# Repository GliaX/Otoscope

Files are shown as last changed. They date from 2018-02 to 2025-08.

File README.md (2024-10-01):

Otoscope
========
This project aims to create a research-validated otoscope whose plans are
available freely and openly. The goal price is approximately USD$3 in parts. The current price is approximately USD$5.

Watch the trailer (https://youtu.be/aX0nkcNqGiI)

This design is based on current gold-standard designs of premium-brand
otoscopes.

The original design and work is by the talented Frankie Talarico. The license
is [TAPR OHL](https://github.com/GliaX/Otoscope/blob/master/LICENSE) where applicable.

* [Bill of Materials](docs/BILL_OF_MATERIALS.md)
* [Print guide](docs/PRINT_GUIDE.md)
* [Assembly instruction video](https://youtu.be/9h2voI1ipZM)
* [Lens assembly guide](docs/LENS_ASSEMBLY.md)
* [Otoscope assembly guide](docs/ASSEMBLY.md)

For an alternative speculum holder (like the one used by Spengler), please see this folder [here](https://github.com/GliaX/Otoscope/tree/master/speculum%20adapter).

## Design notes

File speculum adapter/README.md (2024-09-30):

printing informations: support required to ensure a good shape of the hole
the base shape has to be properly debured because it's a tight fit to ensure the stability of the adapter.

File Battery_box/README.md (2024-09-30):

printing informations: support required to ensure a good shape of the holes

It maintains the original size of the recommended one, ensuring a perfect fit in the "Battery holder".

To further improve cost-effectiveness and reduce dependency on online material ordering, there are two versions of electrical connections. One utilizes a self-made spring from any conducting metal wire, soldered to the wires. The other version uses parts purchased on Amazon for less than a dollar per set.

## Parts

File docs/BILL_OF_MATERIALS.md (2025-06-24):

Is a Link down? Tell us, and in the meantime while we fix it, google the listing title below to find the item/ alternatives. 

## AA battery case
#### Needs to be this exact model, due to the tight fitting nature on the holder in the 3D printed compartment
* [[Digikey](https://www.digikey.ca/product-detail/en/mpd-memory-protection-devices/BC12AAW/BC12AAW-ND/2439232) $1.90]

## 2.7 ohm resistor 
* [[Amazon](https://www.amazon.ca/dp/B0185FHBGC?ref=ppx_yo2ov_dt_b_fed_asin_title) $0.09]

## 5mm LED light
#### Really, any 5mm bright white LED could be used.  I like the one listed below because it is much brighter than any other LED light I've used.  Check the voltages of the LED you use, if the LED is rated for less that 3.2V, reassess which resistor you put into the circuit. 
* Amazon listing for the LED, listing titled "100pc 5MM White Round Water Clear Ultra Bright LED Light Diodes 30000 mcd - 40000 mcd (White)" [[Amazon CA](https://www.amazon.ca/100pc-White-Round-Bright-Diodes/dp/B0781Z96S6) $0.11 ($11.97/100pc)]

## Rocker Switch
#### Needs to be this model's dimension, due to the tight fitting nature of the switch in the 3D printed compartment
* Ebay listing for switch, listing titled "20x 250V 3A Mini Boat Rocker Switch SPST ON-OFF KCD1-2Pin Black Plastic Button" [[Ebay](https://www.ebay.com/itm/20x-250V-3A-Mini-Boat-Rocker-Switch-SPST-ON-OFF-KCD1-2Pin-Black-Plastic-Button-/141819484825) $0.25 ($5.00/ 20pc)]
* Ebay listing for switch, listing titled "10pcs Small Mini Black On/Off Boat Rocker Switch Rectangle10x15mm-SPST-2PIN V9A3" [[Ebay](https://www.ebay.ca/itm/10pcs-Small-Mini-Black-On-Off-Boat-Rocker-Switch-Rectangle10x15mm-SPST-2PIN-V9A3/264334026704?ssPageName=STRK%3AMEBIDX%3AIT&_trksid=p2057872.m2749.l2649) $0.15 ($1.55/ 10pc)]
* AliExpress Listing for switch, listing titled "10 pcs/lot KCD1 15 10mm 2PIN Boat Rocker Switch SPST Snap-in on off Micro switch Position 3A/250V Mini" [[Aliexpress](https://www.aliexpress.com/item/32880358926.html?spm=2114.search0302.3.1.5a7a118e4QEAbi&ws_ab_test=searchweb0_0,searchweb201602_0_10130_453_454_10618_536_317_537_319_10059_10696_10084_10083_10547_10546_10887_10307_321_10548_322_10065_10068_10103_10884_10545,searchweb201603_0,ppcSwitch_0&algo_pvid=8fdccf1d-54b3-4fad-b18d-6b211bd21dcf&algo_expid=8fdccf1d-54b3-4fad-b18d-6b211bd21dcf-0) $0.09 ($0.92/ 10pc)]

## 3x magnification lens
#### Below are two links to lenses that would work with the otoscope.  Following the [Lens Assembly Guide](https://github.com/GliaX/Otoscope/blob/master/docs/LENS_ASSEMBLY.md), you should manipulate the lens to fit in the holder. The Amazon listing below is the lens that fits the [new_lensjig2024.stl](https://github.com/GliaX/Otoscope/blob/master/lens_jig/new_lensjig2024.stl) part.  I recommend also checking local department stores for these items too. They can go by the name of "pocket reader", "3x magnifier with LED", and "Easy reader".  

* Ebay Listing for a pocket reader, listing titled "A Credit Card LED Magnifier Loupe with Light Case Magnifying Glass Utility [[Ebay](https://www.ebay.com/p/Credit-Card-LED-Magnifier-Loupe-With-Light-Leather-Case-Magnifying-Glass-Utility/3029465108?iid=362601347786&rt=nc) $2.39] 

* Amazon Listing for small 3x magnifying glasses, listing titled "Handheld Magnifier with Safety Lanyard (Set of 10)" [[Amazon CA](https://www.amazon.ca/gp/product/B008AK673Q/ref=ppx_yo_dt_b_asin_title_o01_s00?ie=UTF8&psc=1) $1.96 each]

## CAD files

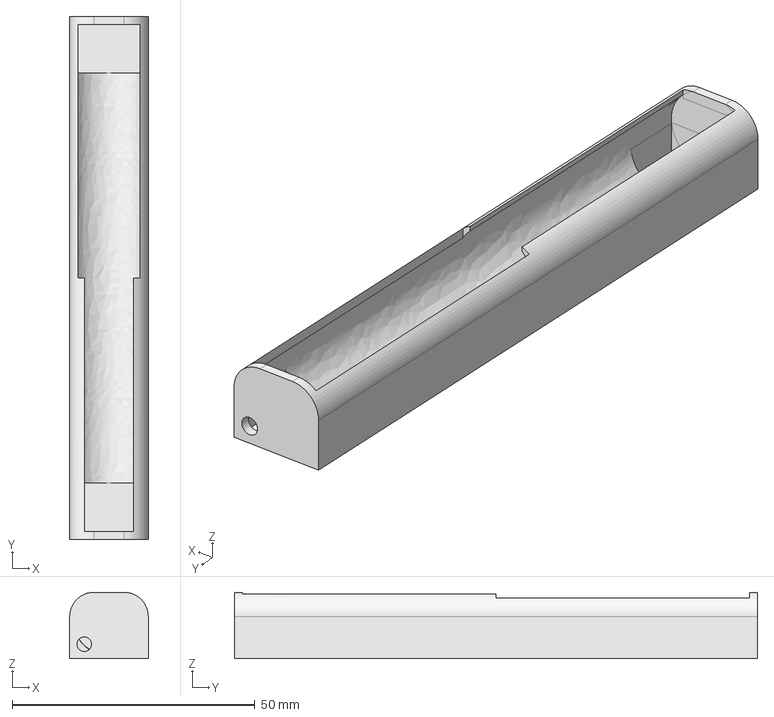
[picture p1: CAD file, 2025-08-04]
Battery_box/source file/Battery Box V3.fcstd
16.2 x 107.8 x 13.7 mm

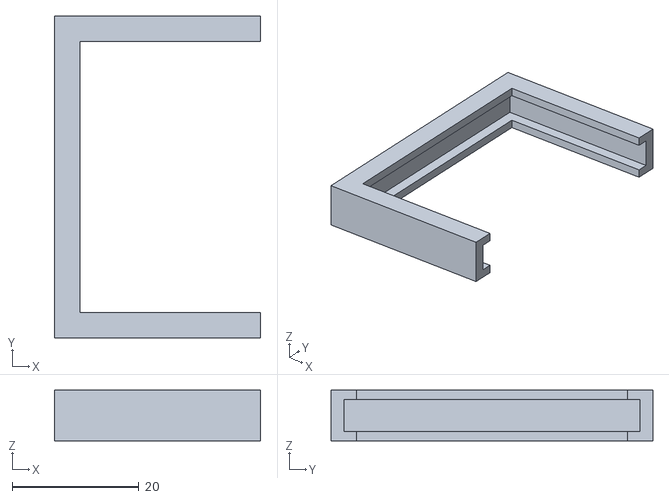
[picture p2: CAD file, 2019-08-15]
lens_jig/jig_1.stl
32.5 x 50.8 x 8.00

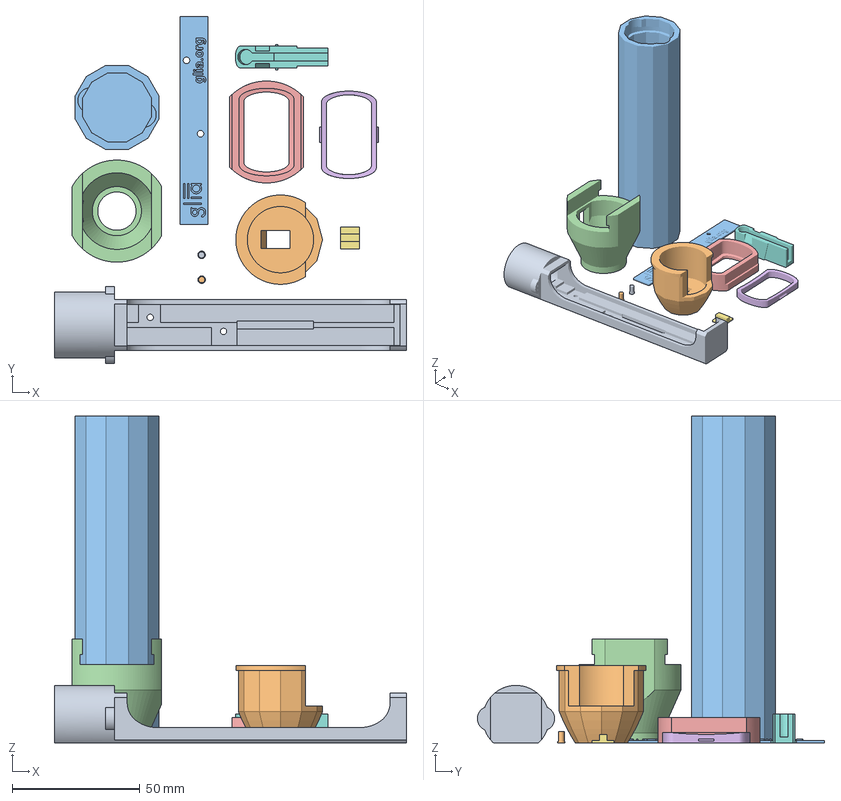
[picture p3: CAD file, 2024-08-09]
otoscope.3mf
137.9 x 136.1 x 128.0 mm
battery_holder.stl
button_cover.stl
handle.stl
head.stl
lens_large.stl
lens_small.stl
neck_cover_plate.stl
neck_led_holder.stl
plate_pin.stl
glia_name_plate (only logo and website).stl

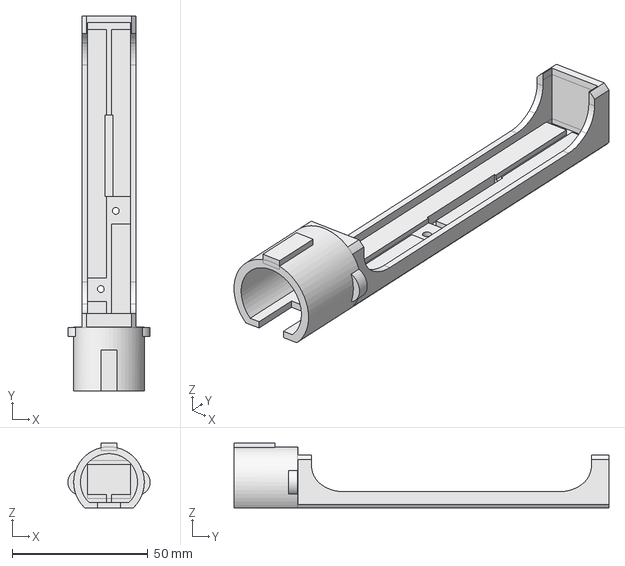
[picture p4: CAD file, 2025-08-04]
source_files/battery_holder2.FCStd
30.3 x 138.0 x 23.9 mm

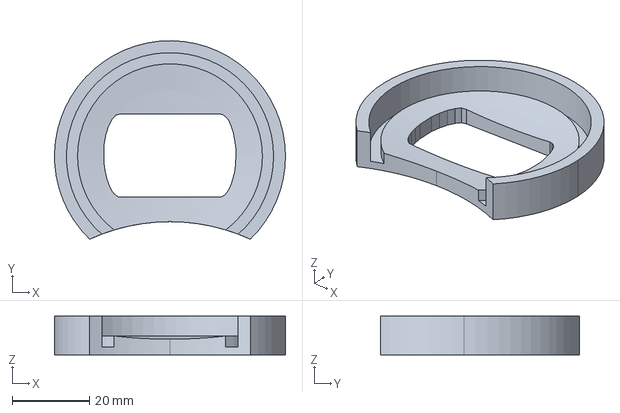
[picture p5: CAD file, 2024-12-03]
source_files/lens_jig/new_lensjig2024.FCStd
60.0 x 51.6 x 10.0 mm

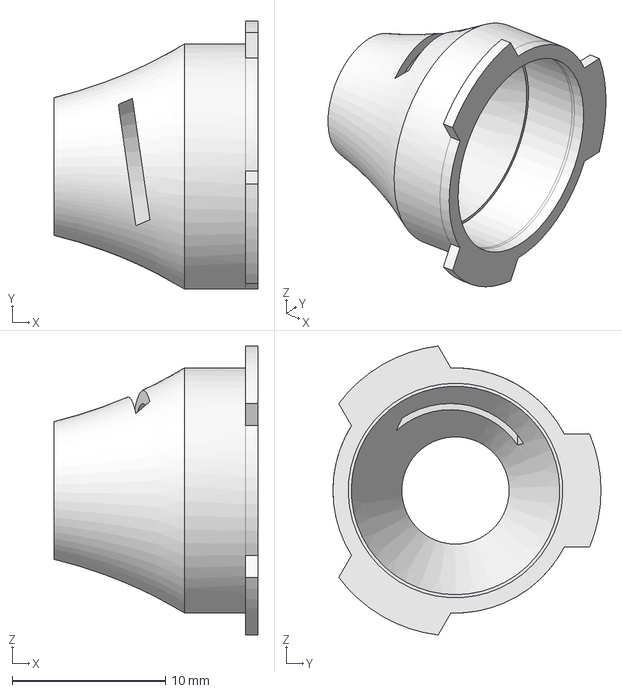
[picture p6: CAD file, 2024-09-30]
speculum adapter/source files/adaptater.FCStd
13.3 x 17.5 x 18.9 mm

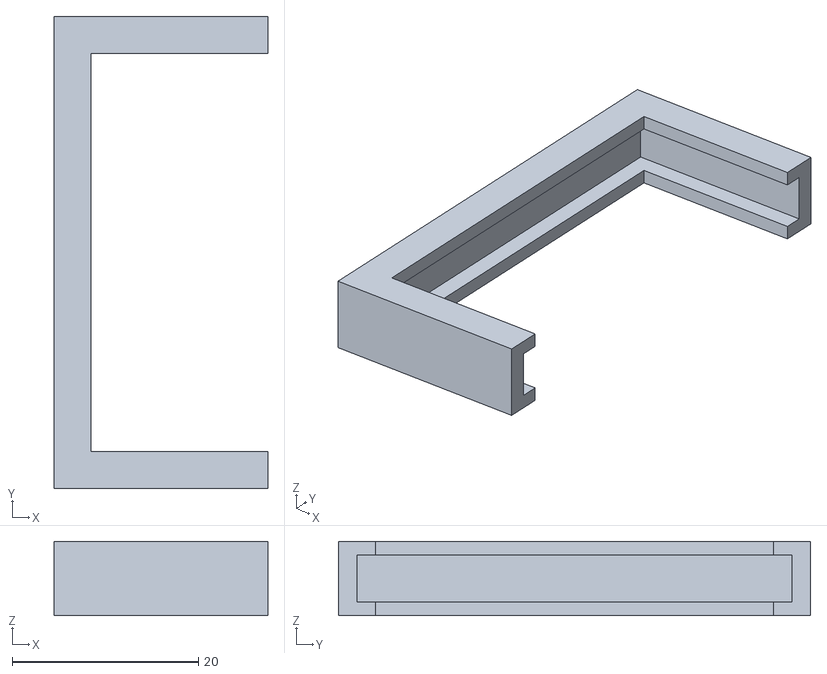
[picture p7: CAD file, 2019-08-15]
lens_jig/jig_2.stl
23.0 x 50.8 x 8.00

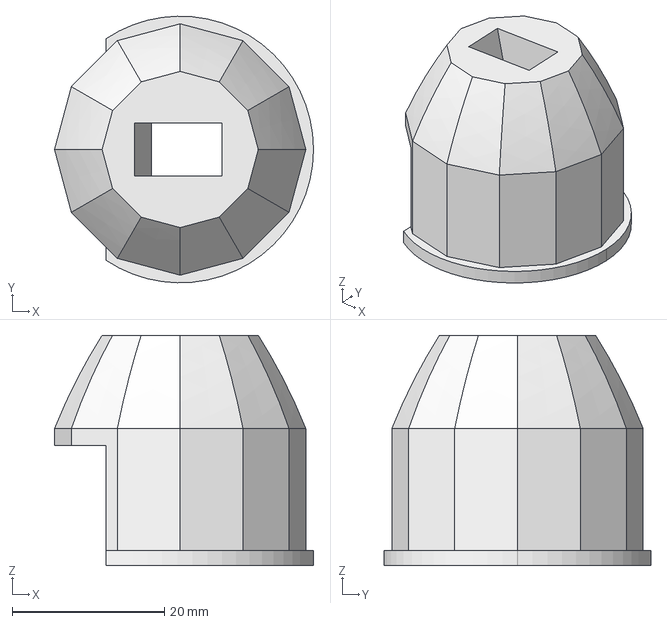
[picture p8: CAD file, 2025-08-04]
source_files/button_cover2.FCStd
34.0 x 35.0 x 30.3 mm

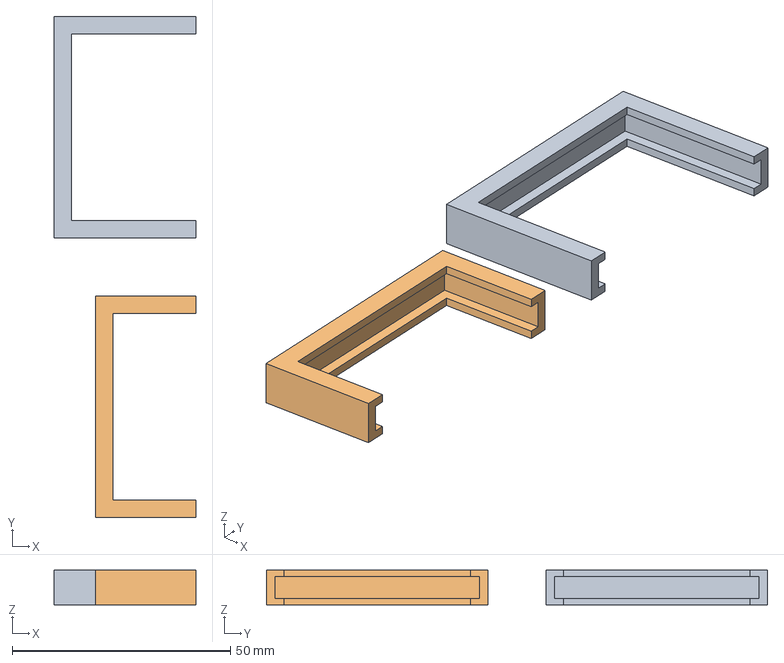
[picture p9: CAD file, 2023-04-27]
source_files/lens_jig/lens_jig.FCStd
32.5 x 114.8 x 8.00 mm
jig_1_src
jig_2_src

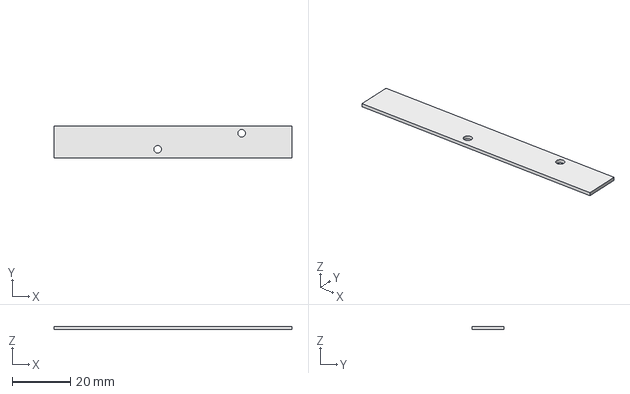
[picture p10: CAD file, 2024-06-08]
source_files/label_plate.FCStd
81.5 x 11.0 x 1.00 mm

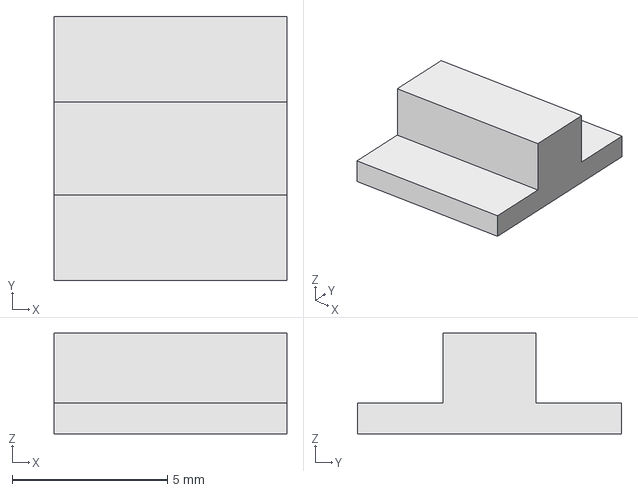
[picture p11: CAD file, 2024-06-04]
source_files/neck_cover_plate.FCStd
7.50 x 8.50 x 3.25 mm

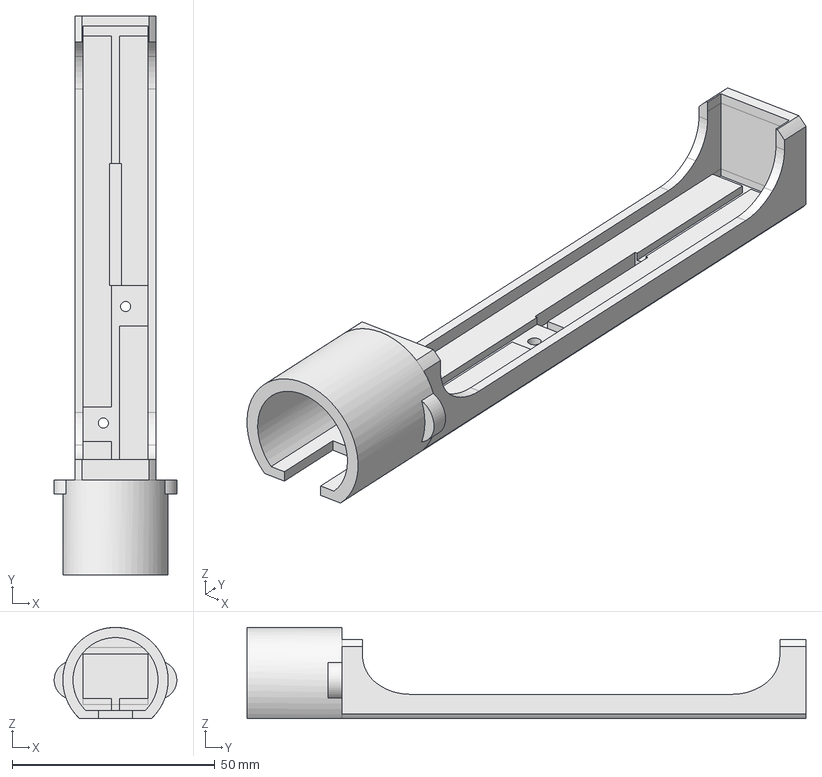
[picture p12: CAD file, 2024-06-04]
source_files/battery_holder.FCStd
30.3 x 137.9 x 22.5 mm

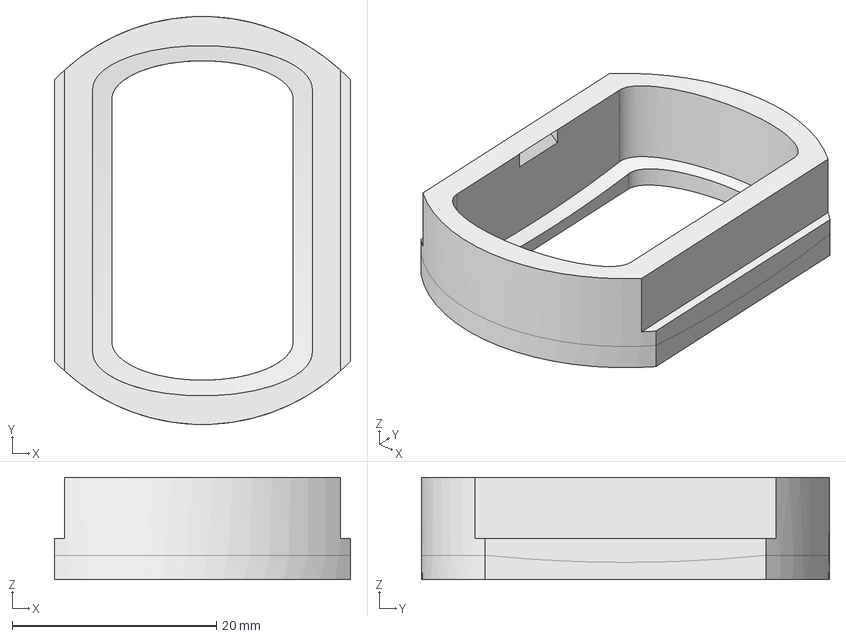
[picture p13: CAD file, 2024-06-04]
source_files/lens_large.FCStd
29.0 x 40.0 x 10.0 mm

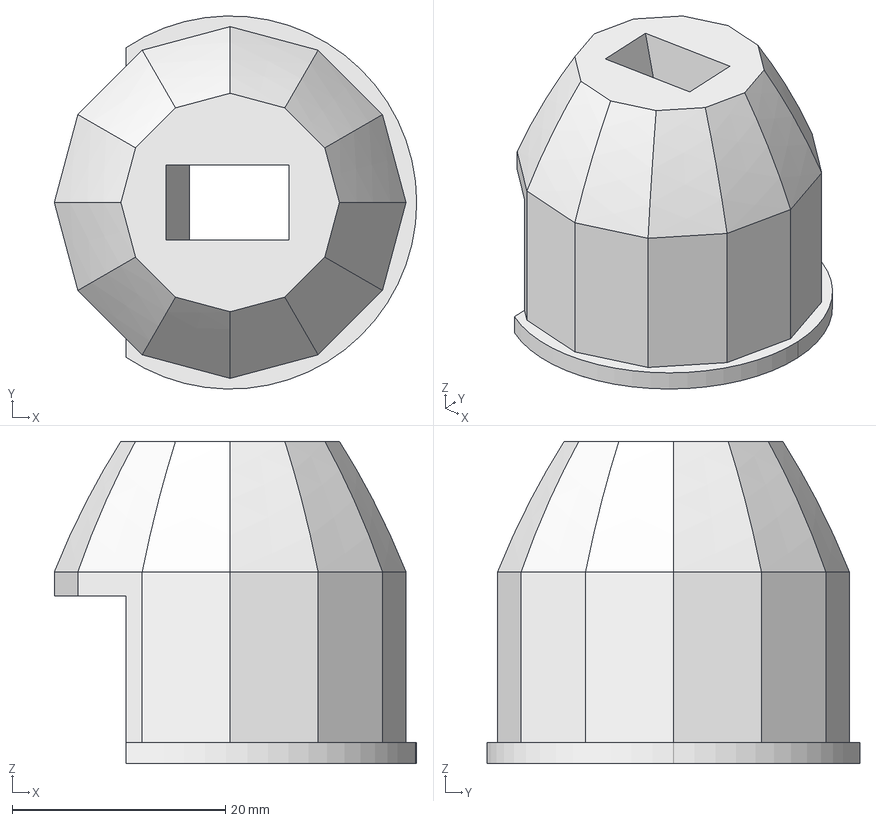
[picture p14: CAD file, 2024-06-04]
source_files/button_cover.FCStd
34.0 x 35.0 x 30.3 mm

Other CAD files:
Battery_box/source file/BatteryBoxV3-Corps.stl
source_files/neck_led_holder.FCStd
source_files/plate_pin.FCStd
source_files/head.FCStd
battery_holder.stl
button_cover.stl
handle.stl
head.stl
label_plate.stl
lens_jig/new_lensjig2024.stl
lens_large.stl
lens_small.stl
neck_cover_plate.stl
neck_led_holder.stl
plate_pin.stl
source_files/handle.FCStd
source_files/lens_jig/jig_1.obj
source_files/lens_jig/jig_2.obj
source_files/lens_small.FCStd
source_files/specula.FCStd
specula.stl
speculum adapter/source files/adaptater.stl

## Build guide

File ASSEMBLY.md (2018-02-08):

# Otoscope Assembly Guide

This document outlines the manufacture of a high-quality low-cost open source otoscope. In this document, we will assemble main otoscope body, including the otoscope head, neck and battery area. Lens creation is [covered in a separate guide](LENS_ASSEMBLY.md).

You will need the following:

* Printed parts:
  * Battery holder
  * Button holder
  * Handle cover
  * Inner head
  * LED chamber
  * Outer head

* Other parts:
  * Completed [lens assembly](LENS_ASSEMBLY.md)
  * Battery compartment x 2 ([amazon]())
  * Momentary switch ([amazon]())
  * 
  * Cyanoacrylate glue ([amazon](https://www.amazon.ca/Gorilla-7805201-20g-Super-Glue))
  * Clamps ([amazon](https://www.amazon.ca/TEKTON-3901-4-Inch-Opening-10-Piece))

## Step 1
Prepare printed parts and acquire other parts as necessary. Below are all required printed parts except for the handle cover and the bottom half of the LED chamber. All pieces should be printed in black, but the LED chamber top can be printed in white for extra LED light reflectance. 

Parts for otoscope assembly

## Step 2
Sand the bottom of the neck piece and the square holder area of the battery holder. Sand or file the connector appendage until a tight fit is achieved.

Battery and neck pieces

## Step 3
Glue the neck piece and the battery compartment

Assembled battery and neck pieces

## Step 4
Prepare battery compartment. Roughly sand bottom of battery compartment for better glue exposure. 

Battery compartments with wiring
Battery compartments with soldering between

## Step 5
Place wiring through the slot in the battery holder. Glue the battery compartments to the battery holder.

Battery compartments with wiring through battery holder
Battery compartments glued to battery holder

## Step 6
Prepare button.
	
Feed button wires through the button holder.  Placed button in the button holder and super glue.

Solder one button wire to the positive wire from battery holders. 

Create the LED chamber.

I placed a 220 ohm pull-up resistor here, I took this out after the fact because the lights were too dim. 

Super glue LED chamber bottom half. 
Super glue LED chamber to the otoscope inner head. 

Feed wires through otoscope neck conduit.  Place otoscope inner head inside the otoscope outer head. 

Super glue the inner head piece on the outer head piece. 

Connect otoscope head to battery part. 

Slide excess wire into neck section of otoscope. 
Super glue the two parts.

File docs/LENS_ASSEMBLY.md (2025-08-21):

# **Lens Assembly Guide**

*This document explains how to make the lens for the current version of the Glia Otoscope.*

You will need the following:
         
        3D Printed Parts:
        ◦ Lens holder (large)
        ◦ Lens holder (small)
        ◦ Lens jig  (new_lensjig2024.stl)
        
        Other:
        ◦ Lens, 3x magnification 
        ◦ Masking tape
        ◦ Pen or fine marker
        ◦ Saw
        ◦ Sander

**Step 1**

Cover back and front of lens with masking tape to protect it.

lens with tape on it

**Step 2**

Place lens jig over lens. Use pen or fine marker to trace shape onto lens, as close to lens jig as possible. Then take lens jig off of lens.

jig on lens trace outline

pen outline

**Step 3**

Carefully use a saw to roughly cut out the traced shap, keeping just outside of traced line. 

cut out lens

**Step 4**

Carefully use sander to refine cut out lens so that it will fit snugly into large lens holder. It is recommended to go slow, and try the fit after each time you sand to make sure you get a snug fit and don’t sand the lens too small. Sand the lens to get as close to the traced line as possible.

There should not be any gaps between the lens and the large lens holder.

lens in lens holder

**Step 5**

Once the lens fits snugly into the large lens holder, carefully take off the masking tape without touching the face of the lens, and push it all the way into the large lens holder. Then push the small lens holder in to secure the lens in the holder.

The fit should be snug enough that you do not need to secure the lens in the holder with glue.

tape off lens small lens holder holding in lens

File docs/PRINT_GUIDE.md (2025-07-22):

# Print Guide

This document explains how to orient and print the various printed parts. This guide uses [Slic3r](http://slic3r.org/)

## Print settings

All parts (other than the handle) should be printed with an infill of 100% and layer height of 0.2mm.  

*The handle should be printed with an infil of 20%.*

A couple of tips when printing in Petg:
<br>
If you have trouble getting the battery_holder and handle to fit properly, print the handle at 2% larger, and the battery_holder at 1% smaller (the wired battery case should still fit when the bottom edges are trimmed). If you have trouble getting the neck_led_holder to fit the button cover, print it at 2% smaller (and then print the neck_cover_plate at 2% smaller as well so that it will fit the led holder).

## Supports

The following parts can be printed without any supports from the 3mf file uploaded:
  * Handle
  * Label plate
  * Lens large
  * Lens small
  * Neck cover plate
  * Neck led holder
  * Plate pins
  * Button cover
  
The following should be printed with supports:
  * Battery holder (full supports)
  * Head (supports on build plate only)

## Orientation
Orient the parts as in the build plate below:
Slic3r bed with all parts

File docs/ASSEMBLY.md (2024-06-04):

# Otoscope Assembly Guide

This document outlines the manufacture of a high-quality low-cost open source otoscope. In this document, we will assemble main otoscope body, including the otoscope head, neck and battery area.

You will need the following:

* Printed parts (See [Print guide](/docs/PRINT_GUIDE.md)):
  * Handle
  * Battery Holder
  * Head
  * Button Holder
  * Label Plate
  * Lens Large
  * Lens Small
  * Neck Cover Plate
  * Neck LED Holder
  * Plate Pins

* Other parts:
  * 3x acrylic lens
  * AA Battery holder 
  * Switch 
  * 5mm LED light 
  * Cyanoacrylate glue 
  * Soldering iron
  * Solder
  * Small gauge wire
  * Electrical tape or shrinkwrap wire cover

Watch the youtube video tutorial here on how to build the otoscope:
https://youtu.be/9h2voI1ipZM

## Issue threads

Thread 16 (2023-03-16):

### ISSUE TITLE
Suggested simplified versions of 2 CAD files from forum

### ISSUE THREAD

**Issue by tareko** [GliaX/Otoscope#16]
Hello @0penBrain and @mwganson.

User `kisolre` on the FreeCAD forums submitted "[a simplified sketch of the specula_holder](https://forum.freecadweb.org/viewtopic.php?f=8&t=38643&p=330601#p330584)" and a "[head lock recreated in PartDesign with proper ellipses](https://forum.freecadweb.org/viewtopic.php?f=8&t=38643&p=330601#p330597)".

Could you guys comment on whether these files supersede yours or what I should do about this?

Thank you

tarek : )

**Comment by mef51** [comment]
I've modified kisolre's `head_lock` model with parabolas instead of ellipses and added a longer tail as part of the assembly changes in PR #19.

I've also updated the main branch with kisolre's simpler sketch in `specula_holder` and simplified the pocket features

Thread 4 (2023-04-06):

### ISSUE TITLE
Why are there no CAD files?

### ISSUE THREAD

**Issue by luzpaz** [GliaX/Otoscope#4]
I'm part of the FreeCAD community outreach team. There are a lot of volunteers on the forum that could be willing to help in this very cool endeavor. Feel free to post on our [Forums](https://forum.freecadweb.org/) to showcase your work or ask for help. 

Examples:  
* [3D printed canine hind limb](https://forum.freecadweb.org/viewtopic.php?t=26901)
* [Anyone interested in donating their time to make a clubfoot brace?](https://forum.freecadweb.org/viewtopic.php?t=27168)  
* [Open Source Ecology](https://wiki.opensourceecology.org/wiki/FreeCAD_101) onboards their community with FreeCAD  
etc...

**Comment by tareko** [comment]
Thank you so much @luzpaz ! I'll look and post in the next day or two.
Our experience is such a testament to the need for FreeCAD, and why we base our work on FreeCAD and OpenSCAD as well. Thank you!

**Comment by eddriesen** [comment]
I'm creating the files as we speak. Please do mind that freecad is new to me. So bare with me. 
 
Things i'm figuring out atm.;
- part / body / project structure
- ok to use assembly2 module (prime time?/ Getting an error on 0.18.3)
- seperate proj file for each component vs project file with multiple parts or bodies vs seperate files and assembly2 project file
- any topdown / associativity possible?

**Comment by luzpaz** [comment]
No, Assembly2 is deprecated. Better to use Assembly2+ or Assembly3.  
Please open a thread on the FreeCAD forums to discuss with the community. Thanks!

**Comment by tareko** [comment]
Thanks for the advice @luzpaz . Will open the thread tonight and post here.

**Comment by tareko** [comment]
[Posted to the FreeCAD forums](https://forum.freecadweb.org/viewtopic.php?f=31&t=38643)

**Comment by rewolff** [comment]
I read you wanted help in converting to openscad (or freecad which I don't know). 
I have started a bit, but it is much more difficult than expected. For example, The "button_block" looks as if it is the difference between three rectangular blocks (with critical parameters 18.45, 1.398, 12.747 and 13.000) and a sphere. But it turns out that sphere is not a sphere. So.... To help me: What kinds of shapes are involved in an object like the button_block ???

**Comment by tareko** [comment]
Hi @rewolff! Just a quick note that there seems to be an active effort to do this in FreeCAD at the moment, which I think is more fit for purpose. You are welcome to continue in OpenSCAD, but you may feel this work is duplicating the work of others.

Regarding your specific query, I have poked @Frankie-E4Rdesigns about this to answer you more specifically. I don't think your replica is obliged to be 1:1, though obviously the pieces will have to fit together in the end.

Thank you again!

tarek : )

**Comment by Frankie-E4Rdesigns** [comment]
Specula Holder, Handle cover, button lock, neck part, button block, and handle coupler all look great!

**Comment by tareko** [comment]
OK, I figure instead I'm going to get rid of the PRs above and keep a list of TODO parts. This is a duplicate of the FreeCAD thread's list.. I'll keep it on the [first post I made](https://github.com/GliaX/Otoscope/issues/4#issuecomment-521977767).

**Comment by 0penBrain** [comment]
@tareko : regarding both lens holders, as it can be some critical parts, I think it is necessary that we can get a 3D model or mechanical drawing of the lens itself (or eventually some optical/mathematical description of it). May you provide that ?

**Comment by Frankie-E4Rdesigns** [comment]
Good idea on the lens schematics, will post something on that soon. 
Different 3x magnification lenses will have slightly different dimensions, but I will post about the one I use.

**Comment by mef51** [comment]
PR #19 adds freecad files for
* inner_head
* outer_head
* lens_holder_bottom

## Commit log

2015-04-01 initial commit of phone-mounted otoscope setup
    [phonemountotoscope.scad, phonemountotoscope.stl]
2018-01-25 Replace old files with new standalone model
    [battery_holder.stl, button_holder.stl, inner_head.stl, led_chamber.stl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]
2018-01-25 Add handle cover
    [handle_cover.stl]
2018-02-07 Add OBJ source files for STLs
    Exported directly from TinkerCAD with the materials removed
    [battery_holder.obj, button_holder.obj, handle_cover.obj, inner_head.obj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]
2018-02-07 Add lens jig STL and source files
    [jig_1.obj, jig_1.stl, jig_2.obj, jig_2.stl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]
2018-02-07 First iteration of Assembly document as written by @Frankie-E4Rdesigns
2018-02-07 Add lens assembly instructions
2018-02-07 First version of Assembly instructions as written by @Frankie_E4RDesigns
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2018-02-09 Repaired STL
    [inner_head.stl]
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2019-08-14 Upgrade to version 3.0 files
    [battery_holder.obj, battery_holder.stl, button_block.obj, button_block.stl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]
2019-08-15 Update to new jig files
    [jig_1.obj, jig_1.stl, jig_2.obj, jig_2.stl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]
2019-08-15 Add Otoscope plate as 3MF
    [otoscope.3mf]
2019-08-26 head_lock, name_plate, name_plate_locks
    [head_lock.FCStd, name_plate.FCStd, name_plate_locks.FCStd]
2019-08-27 tilt head_lock 3 degrees
    [head_lock.FCStd]
2019-08-27 tile head_lock 3 degrees
    [head_lock.FCStd]
2019-08-27 Move all files to regular source and adapt name_plate to relative paths
    [head_lock.FCStd, name_plate.FCStd, name_plate_locks.FCStd]
2019-08-28 specula_holder initial release => check geometry OK
    [specula_holder.FCStd]
2019-08-28 handle cover => Check geometry OK // Splines approximated with arcs
    [handle_cover.FCStd]
2019-08-28 button lock initial release => Check geometry OK
    [button_lock.FCStd]
2019-08-28 neck part initial release => Check geometry OK
    [neck.FCStd]
2019-08-28 button block initial release => Check geometry OK
    [button_block.FCStd]
2019-08-29 remove a useless remaining object used for modeling
    [button_lock.FCStd]
2019-08-29 button holder initial release
    [button_holder.FCStd]
2019-08-30 Move to proper source folder
    [specula_holder.FCStd]
2019-08-30 Move to correct source_files folder
    [handle_cover.FCStd]
2019-08-30 Move files to correct source folder
    [button_block.FCStd, button_lock.FCStd, neck.FCStd]
2019-08-30 button holder bottom initial release
    [button_holder_bottom.FCStd]
2019-08-30 Add lens jig from Kisolre
    [lens_jig.FCStd]
2022-12-06 add glia name plate
    [glia_name_plate.FCStd, glia_name_plate.stl]
2023-01-16 import outer_head into freecad and make one lock larger for easier assembly
    [outer_head_largerlock.3mf, outer_head_largerlock.FCStd, outer_head_largerlock.stl]
2023-01-18 add clearance on inner head edge, extend head lock tail, larger head hole
    [head_lock.FCStd, head_lock.stl, inner_head.stl, outer_head_import.FCStd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]
2023-01-18 add clearance to inner head edges and flatten bottom of outer head lock hole
    [inner_head.stl, outer_head_import.FCStd, outer_head_largerlock.stl]
2023-01-24 add backing to bulb feed on inner head for better printing.
    fix broken stl of outer head
    [inner_head.stl, outer_head_import.FCStd, outer_head_largerlock.stl]
2023-02-01 add remodel of inner head
    [inner_head.FCStd]
2023-02-02 fix topo naming problem on inner head
    [inner_head.FCStd]
2023-02-07 add model of lens_holder_bottom.
    Freecad boolean doesn't seem to work so no spherical contour for the lens
    [lens_holder_bottom.FCStd]
2023-02-07 add lens_holder_bottom thanks to Shalmeneser on freecad forums
    https://forum.freecad.org/viewtopic.php?p=659133#p659133
    [lens_holder_bottom.FCStd, lens_holder_bottom.stl]
2023-02-08 add remodel of outer head
    [outer_head.FCStd, outer_head.stl, outer_head_largerlock.stl]
2023-02-14 adjust outer and inner heads for assembly
    [inner_head.FCStd, inner_head.stl, lens_holder_bottom.FCStd, outer_head.stl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]
2023-02-15 add lens_holder_top, remove imported freecad meshes,
    [lens_holder_top.FCStd, lens_holder_top.stl, outer_head_import.FCStd]
2023-02-20 remodel battery holder in freecad
    [battery_holder.FCStd, battery_holder.stl]
2023-03-16 move button_holder and add stl from freecad file
    [button_holder.FCStd, button_holder.stl]
2023-03-16 move button_holder_bottom and add stl
    [button_holder_bottom.FCStd, button_holder_bottom.stl]
2023-03-16 add freecad model of handle_coupler
    [handle_coupler.FCStd, handle_coupler.stl]
2023-03-16 import kisolre's head_lock, replace ellipses with parabolas, extend tail
    original file from
    https://forum.freecad.org/viewtopic.php?f=8&t=38643&p=330601#p330597
    part of issue #16
    [head_lock.FCStd, head_lock.stl]
2023-03-16 update specula_holder model with kisolre's sketch, simplify pockets
    kisolre's sketch:
    https://forum.freecad.org/viewtopic.php?f=8&t=38643&p=330601#p330584
    close #16
    [specula_holder.FCStd]
2023-03-16 reload assembly-tweaked stls into otoscope.3mf
    [otoscope.3mf]
2023-03-28 batter_holder: re-add circular divet and cut groove through
    [battery_holder.FCStd, battery_holder.stl]
2023-04-05 adjust models to accomodate LED and circuit switch
    * remodel inner_head to remove topo problem and make bulb case larger
    * match name plate holes to battery holder
    * enlarge neck and button_holder hole for tighter fit
    * enlarge button_holder and button_holder_bottom mate to fit switch
    [button_block.FCStd, button_block.stl, button_holder.FCStd, button_holder.stl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]
2023-04-06 add clearance to battery holder for battery case and update 3mf plate
    [battery_holder.FCStd, battery_holder.stl, otoscope.3mf]
2023-04-17 tighten fit between lens holder and head, and lens. shape head lock.
    [head_lock.FCStd, head_lock.stl, lens_holder_top.FCStd, lens_holder_top.stl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]
2023-04-27 Add freecad model of specula based on welch allyn specula
    [specula.FCStd, specula.stl]
2024-02-13 self made battery box
    Hello,
    To enhance the cost-effectiveness of the otoscope, I have developed a printable version of the battery box instead of the recommended purchase.
    It maintains the original size of the recommended one, ensuring a perfect fit in the "Battery holder".
    To further improve cost-effectiveness and reduce dependency on online material ordering, I have created two versions of electrical connections. One utilizes a self-made spring from any conducting met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
    [Battery box v2.fcstd, Body (Meshed)v2.stl]
2024-05-27 Specula holder adaptation to standard
    Hello
    I made a new version of the specula holder to make it possible to use with the standard disposable specula.
    This kind of speculum is made of smooth plastic that makes it easily washable for sanitary purpose. This model is the most common, with two possible sizes.
    The piece should be mounted with the hole up.
    [Speculum_mod.igs, speculum5.stl]
2024-05-30 add v2 redesign freecad and stl files; fewer components and qol changes
    * remove old designs and stls
    [battery_holder.FCStd, battery_holder.obj, battery_holder.stl, button_block.FCStd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]
2024-06-04 Updated PRINT_GUIDE.md with new parts and print bed image
    Also added new setting for Petg handle, if it doesn't fit.
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2024-06-08 consolidate label plate files
    [glia_name_plate.FCStd, glia_name_plate.stl, label_plate.FCStd, label_plate.stl]
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2024-06-14 New version of battery box
    Same dimensions but stronger and better battery holding
    [Battery Box V3.fcstd, Battery box v2.fcstd, BatteryBoxV3-Corps.stl, Body (Meshed)v2.stl]
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2024-08-09 fixing broken print_bed.jpg image
2024-09-10 new folders organization and specula adapter
    This is a new folders organization for the battery box,
    and i made a specula adapter that fits on the last design to be able to use speculas like spenglers.
    [Battery Box V3.fcstd, BatteryBoxV3-Corps.stl, Speculum_mod.igs, adaptater.FCStd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]
2024-11-05 little modifications on the button cover and battery holder
    I have modified the button cover and the battery holder to add a rail, ensuring proper alignment with the correct axis. I also added a ring around the LED to maintain the correct light angle through 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
    [Battery Box V3.fcstd, LED_ring.FCStd, LED_ring.stl, battery_holder.stl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]
2024-12-03 Update lens listing in BOM
    Took out broken links, and modified text for updated lens assembly instructions and jig.
2024-12-03 adding new_lensjig2024
    This new lens jig fits the amazon lens on the BOM
    [new_lensjig2024.stl]
2024-12-03 adding FreeCAD file of new_lensjig2024
    new lens jig for updated lens assembly guide
    [new_lensjig2024.FCStd]
2024-12-06 try to errase the DS_Store
    [LED_ring.FCStd, LED_ring.stl]
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2025-08-21 Updated lens assembly for current version of otoscope (#31)
    * Update LENS_ASSEMBLY.md
    New updated lens assembly instructions for the current version of otoscope.
    * Update LENS_ASSEMBLY.md
    fixing jpgs in document
    * lens assembly pics from jpg to png
    changing pic extensions
    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
